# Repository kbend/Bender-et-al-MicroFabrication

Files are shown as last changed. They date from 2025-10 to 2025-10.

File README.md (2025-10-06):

# Bender-et-al-MicroFabrication
A repository containing the MATLAB code, Python scripts, CAD files, and tips for the manufacturing procedures for the SLA micropatterning paper by Bender et al (Hsu Lab)

CAD Files
  Stripes - 200, 400, 600, 800            :    STL file for the striped-patterned mold with stripes of 200um, 400um, 600um, and 800um width, respectively
  Checkered Pattern - 200, 400, 600, 800  :    STL file for the checkered-patterned mold with the length of the squares being 200um, 400um, 600um, and 800um, respectively

MATLAB Files
  COA.m   :    MATLAB script that takes a DAPI image, applies a watershed mask, segments, and draws the ellipses, as well as extracts the centroid and orientation values of each ellipse

Protocols
  Resin Printing Protocol    :    A pdf file containing helpful information, tips, and tricks to designing and resin printing custom molds for stamp fabrication
  Stamp Production Protocol  :    A pdf file containing helpful information, tips, and tricks to producing the PDMS stamps
  Stamping Procedure Protocol:    A pdf file containing helpful information, tips, and tricks to producing the micropatterns using the PDMS stamps and a protein solution of choice

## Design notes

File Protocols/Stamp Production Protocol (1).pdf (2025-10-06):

Steps for Stamp Production
1. Prepare the PDMS solution, a ratio of 10:1 base to curing agent was used by Bender et al.
a. Depending on the design of the mold, two of the four walls may be absent to allow for easy stamp removal. Tape or another similar adhesive can be used to form temporary walls to keep the solution in place during the pouring and curing process.
2. Cure the stamp in an oven at 60

oC for 16 hours as outlined in the Bender et al. manuscript.
a. Curing time in the oven will affect stamp stiffness. A longer curing time will lead to a stiffer stamp.
3. When removing the stamp after curing, care should be taken to pull the stamp off in the direction of the pattern if possible to ensure minimal risk for tearing and other destruction to the stamp.

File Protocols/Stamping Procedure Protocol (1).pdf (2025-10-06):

Steps for Stamping
1. Plasma treat the stamp for 30 seconds to induce hydrophilicity
a. When plasma treating the stamp, treatment should not be done for longer than 1 minute 30 seconds to avoid the creation of microcracks in the stamping surface
2. After plasma treating the stamp, a protein solution should be applied as outlined in the Bender et al. Manuscript
a. The coating of the protein must be completed within 20 minutes of plasma treatment, as the hydrophilic nature of the stamp will wear off in that amount of time.
3. Once coating is complete, as much excess protein solution as possible should be removed from the stamp.
a. An aspirating tip can be used to remove the excess liquid, taking care not to touch the surface of the stamp.
b. Should an aspirating tip not be available, a KimWipe can be used.
c. A steady flow of inert air can also be passed over the stamp after removal via a KimWipe or aspiration to help further remove any trace amounts of excess liquid.
4. Tweezers should be used to place the stamp on the chosen surface, and care should be taken not to smear or otherwise move the stamp during the administration or removal of the stamp.
a. A small weight can be used to help apply pressure during the stamping process.

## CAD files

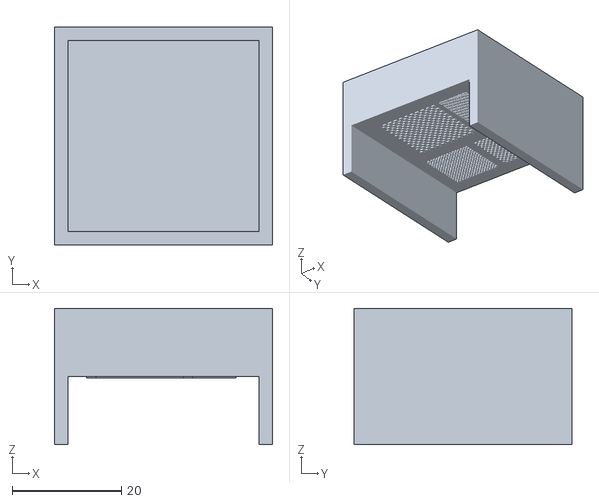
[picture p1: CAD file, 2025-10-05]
STL Files /Checkered Pattern - 200, 400, 600, 800.stl
40.0 x 40.0 x 25.0

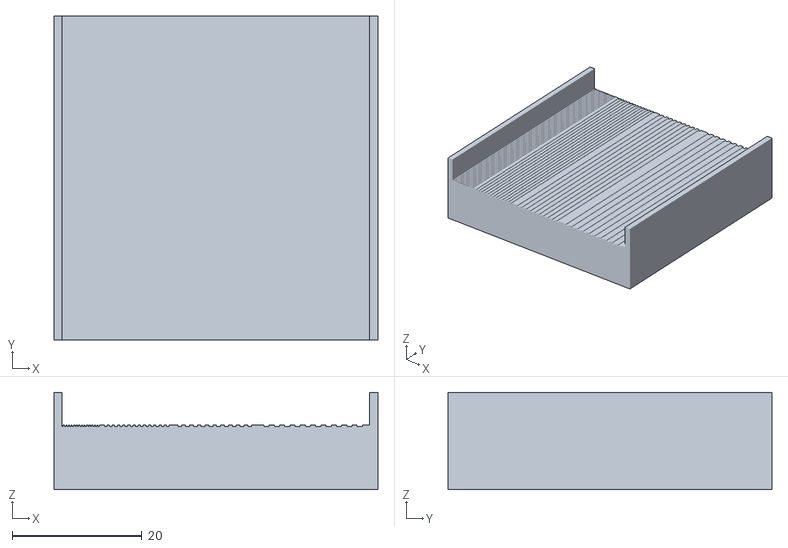
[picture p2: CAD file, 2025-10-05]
STL Files /Stripes - 200, 400, 600, 800.stl
50.0 x 50.0 x 15.0

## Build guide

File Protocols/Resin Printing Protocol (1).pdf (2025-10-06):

Steps for Resin Printing
1. Design the mold of the desired pattern in a CAD software, or use one of the molds provided in the Bender et al. Microfabrication GitHub repository. Some tips and troubleshooting tricks are provided below:
a. Design the mold such that the file is a negative of the desired pattern to ensure the stamp is raised at the correct locations
b. Design the walls surrounding the pattern so that there are walls on only 2 of the 4 sides. This will allow for easy PDMS removal after the curing process. Tape can be used to form temporary walls when pouring in the liquid PDMS.
c. Hollow out the base of the mold. Resin printing does not automatically hollow out solid masses like other forms of 3D printing, and solid objects can consume large amounts of resin. Manually hollowing out the base allows one to save on materials
d. In the molds used by Bender et al., the pattern depth is extruded 300μm, which helps ensure that the pattern is clear but not so fragile that it breaks during the removal process
2. Export the CAD model as an STL and import it into the proper slicing software for the resin printer of choice.
a. The printer with the highest possible resolution should be used for the best results of the pattern.
3. Slice the model according to the printer’s specifications. Some helpful tips concerning slicing:
a. Select the smallest possible layer height
b. Some slicing softwares, such as PreForm, have automatic slicing options. While these options can be helpful, they will often print the file at an angle to help with adhesion issues. This has the unintended consequence of visible layer lines in the print, which can then transfer to the PDMS stamp, leading to uneven micropatterns. To avoid this, manually change the orientation of the file to print on one of the flat surfaces and ensure a smooth top surface
4. Remove the completed print gently, remove supports, and wash off excess resin via an IPA bath prior to the curing process.
5. Some common issues for subpar prints and suggested troubleshooting mechanisms/other factors to consider are listed below:

a. Expired resin: Depending on the type and quality of resin being used, subpar prints may be due to old/bad resin. Resin typically should be used within a year of purchasing and within six months of opening the resin cartridge
b. Textured surface: A textured top surface may be due to visible layer lines (mentioned previously) or the presence of supports on the pattern surface that leave behind noticeable marks upon removal. Visible layer lines can be addressed by rotating the model to lie flat on the printing surface, ensuring a smooth top surface. To remove specific supports, standard slicing softwares come with support blockers, allowing the user to target specific supports for removal.

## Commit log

2025-10-05 Added relevant STL files of molds
    [Checkered Pattern - 200, 400, 600, 800.stl, Stripes - 200, 400, 600, 800.stl]
2025-10-05 Rename Checkered Pattern - 200, 400, 600, 800.stl to STL Files /Checkered Pattern - 200, 400, 600, 800.stl
    [Checkered Pattern - 200, 400, 600, 800.stl]
2025-10-05 Rename Stripes - 200, 400, 600, 800.stl to STL Files /Stripes - 200, 400, 600, 800.stl
    [Stripes - 200, 400, 600, 800.stl]
2025-10-05 Tips for Resin Printing
2025-10-05 Rename Resin Printing Protocol.pdf to Protocols/Resin Printing Protocol.pdf
2025-10-06 Rename Resin Printing Protocol (1).pdf to Resin Printing Protocol.pdf
